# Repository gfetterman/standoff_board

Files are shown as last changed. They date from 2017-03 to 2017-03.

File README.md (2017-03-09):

# Standoff board

This board provides an interface between an [analog headstage](https://github.com/gfetterman/analog_headstage) and Intan amplifiers. It is intended for use in small-animal electrophysiology.

The board currently supports 7 channels, matching the analog headstage linked above.

It also provides the option of stepping down a signal to match the amplifiers' input range. The current schematic provides a 62x attenuation, but any resistor pair may be substituted in the voltage dividers during construction. To pass a signal straight through, without attenuation, replace the appropriate resistor (one of R1-R7) with a jumper cable or zero-Ohm resistor, and remove the corresponding grounding resistor (one of R8-R14).

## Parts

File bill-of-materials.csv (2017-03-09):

supplier | part number | description | quantity
Digikey | CF14JT1K00CT-ND | RES 1K OHM 1/4W 5% AXIAL | 7
Digikey | CF14JT62K0CT-ND | RES 62K OHM 1/4W 5% AXIAL | 7
Omnetics | A79623-001 | PZN-12-AA 12 position polarized nano connector, horiz SMT | 1
Omnetics | A79024-001 | NPD-36-AA-GS 36 position dual row male nano-mini connector, horiz SMT | 1

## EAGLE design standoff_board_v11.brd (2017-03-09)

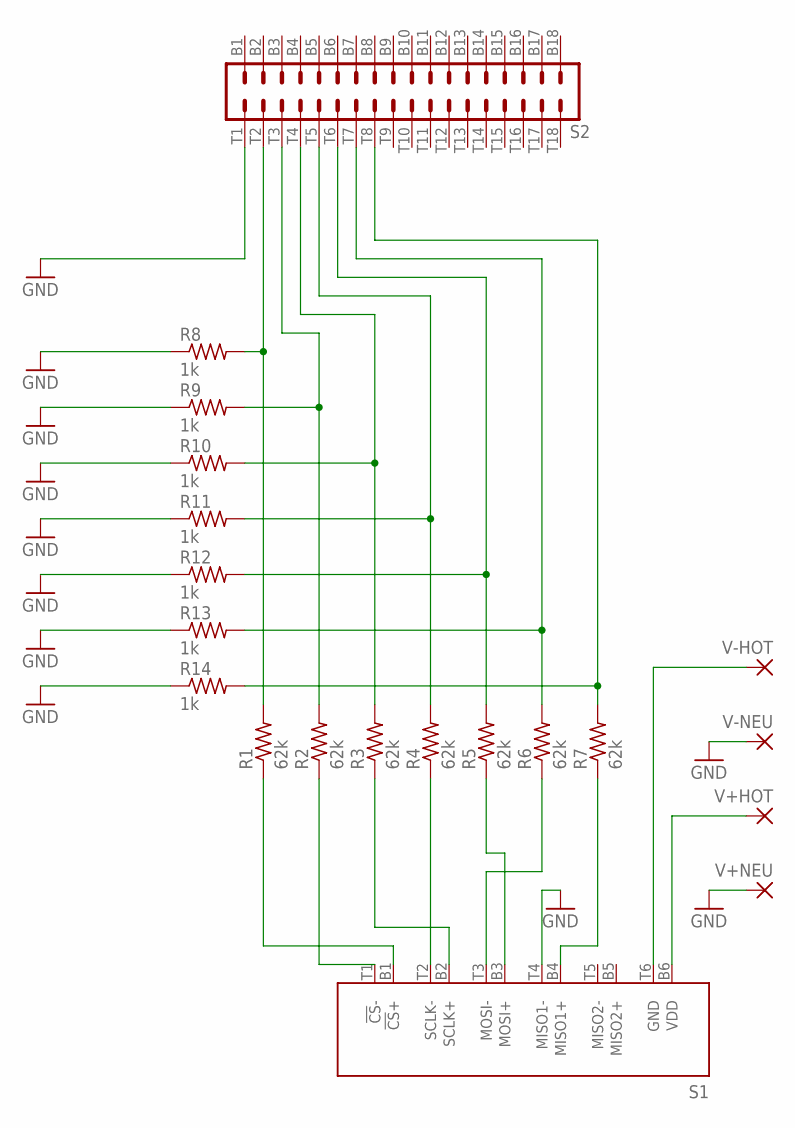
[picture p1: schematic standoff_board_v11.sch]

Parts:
R1, R2, R3, R4, R5, R6, R7: 62k; 0204/7
R8, R9, R10, R11, R12, R13, R14: 1k; 0204/7
S1: RHD2000-CABLE-DAQ-SIDE; OMNETICS_PZN-12-AA
S2: OMNETICS_A79025
V+HOT: 2,54/1,1
V+NEU: 2,54/1,1
V-HOT: 2,54/1,1
V-NEU: 2,54/1,1

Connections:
A1POST: R1.2, R8.2, S2.T2
A1PRE: R1.1, S1.B1 (!CS!+)
A2POST: R2.2, R9.2, S2.T3
A2PRE: R2.1, S1.T1 (!CS!-)
A3POST: R3.2, R10.2, S2.T4
A3PRE: R3.1, S1.B2 (SCLK+)
A4POST: R4.2, R11.2, S2.T5
A4PRE: R4.1, S1.T2 (SCLK-)
A5POST: R5.2, R12.2, S2.T6
A5PRE: R5.1, S1.B3 (MOSI+)
A6POST: R6.2, R13.2, S2.T7
A6PRE: R6.1, S1.T3 (MOSI-)
A7POST: R7.2, R14.2, S2.T8
A7PRE: R7.1, S1.B4 (MISO1+)
GND: R8.1, R9.1, R10.1, R11.1, R12.1, R13.1, R14.1, S1.T4 (MISO1-), S2.T1, V+NEU.1, V-NEU.1
V+HOT: S1.B6 (VDD), V+HOT.1
V-HOT: S1.T6 (GND), V-HOT.1

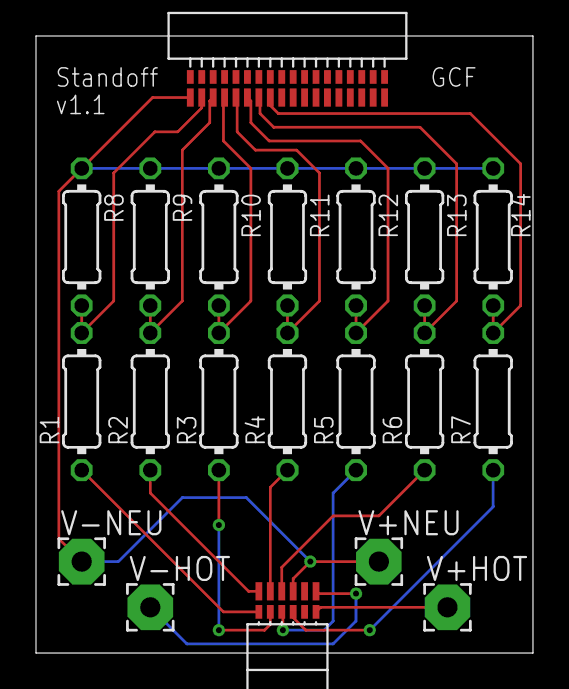
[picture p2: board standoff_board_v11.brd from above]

Board: 2 copper layers, 27.6 x 34.3 mm, 20 parts (0 on the bottom side), 17 nets.

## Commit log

2017-03-09 Reroute output traces symmetrically
    [standoff_board_v11.brd, standoff_board_v11.sch]
2017-03-09 Add bill of materials
    [bill-of-materials.csv]
2017-03-09 Fix typo
    [bill-of-materials.csv]
2017-03-09 Fix NPD-36-AA part number
    [bill-of-materials.csv]
